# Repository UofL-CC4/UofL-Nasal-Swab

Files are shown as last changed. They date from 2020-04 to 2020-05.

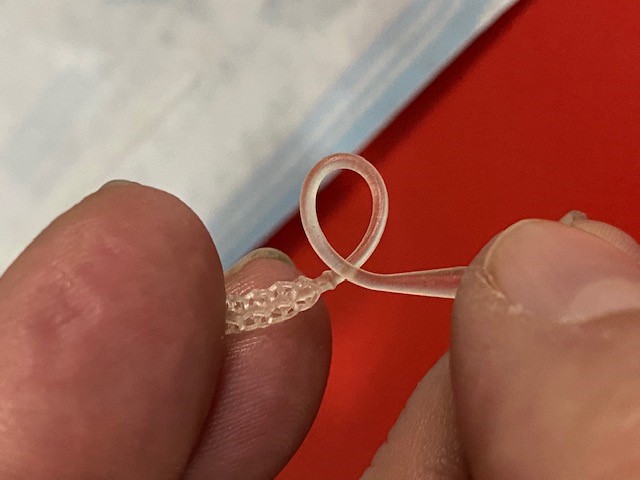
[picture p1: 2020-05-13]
Release R1 05_13_2020/Images/Swab Test.jpg

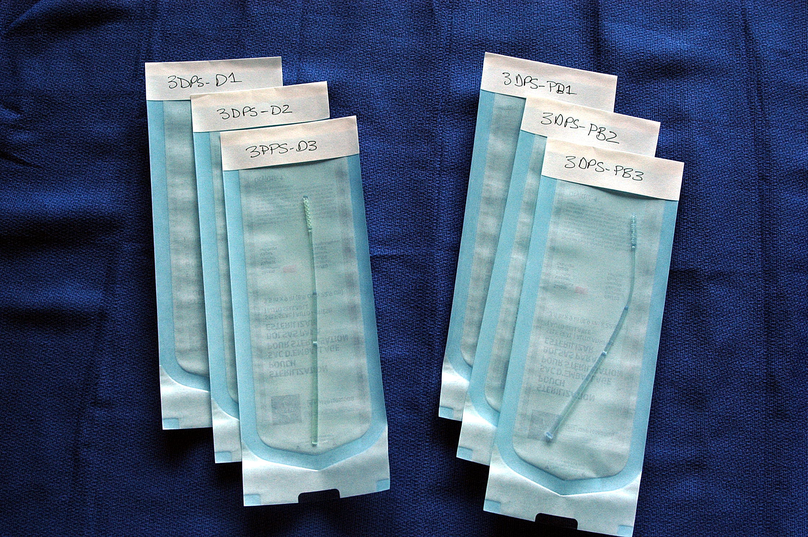
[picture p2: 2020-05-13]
Release R1 05_13_2020/Images/DSC_0561.JPG

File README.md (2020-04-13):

# UofL-Nasal-Swab
UofL Nasal Swab Data Package
We are running (side by side, (Standard Swab/3D Printed Swab)) testing with COVID19 patients to make sure we do not have a problem with false negatives, this is a mandatory clinical trial required by UofL Health Institutional Review Board (IRB).  Under FDA regulations, an IRB is an appropriately constituted group that has been formally designated to review and monitor biomedical research involving human subjects. In accordance with FDA regulations, an IRB has the authority to approve, require modifications in (to secure approval), or disapprove research. This group review serves an important role in the protection of the rights and welfare of human research subjects.

Here is where we are at;
•	We have developed the Creative Commons License for release of all data.
•	There is an online repository for all related files it is live but the final document package is not updated yet. https://github.com/UofL-CC4/UofL-Nasal-Swab
•	All clinical protocols are established and being followed in the IRB Clinical Trial
•	3D printing of the geometry has been clinically validated
•	COVID-19 3D Printed Swab Cleaning Protocol is complete
•	COVID-19 3D Printed Swab Curing Protocol is complete
•	COVID-19 3D Printed Swab Packaging Protocol is complete
•	ETO Sterilization protocol is complete
•	COVID 19 Test Kit Assembly Protocol is complete and SOP is complete
•	Viral transport Medium has been clinically validated using CDC recipe
We are now just waiting for IRB Sign off, we anticipate today.

We are currently building workflows for different 3D printers so we can roll this out Statewide with the current emphasis going to Lexmark and UK.

I have attached 2 videos one is of a completed SWAB print and the second is on the UV curing rack

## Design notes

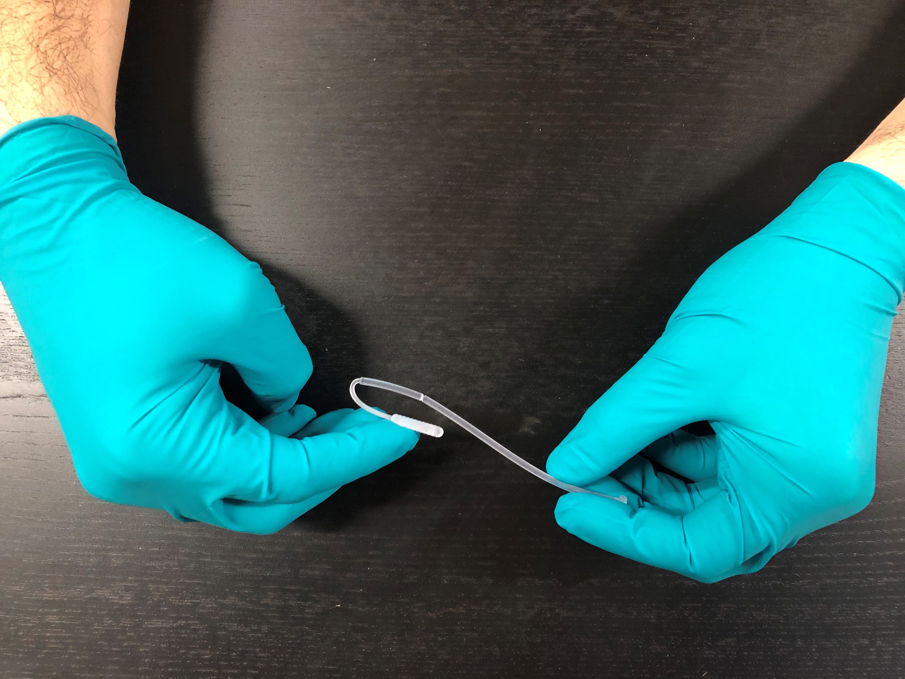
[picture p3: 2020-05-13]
Release R1 05_13_2020/Images/KS003.jpg

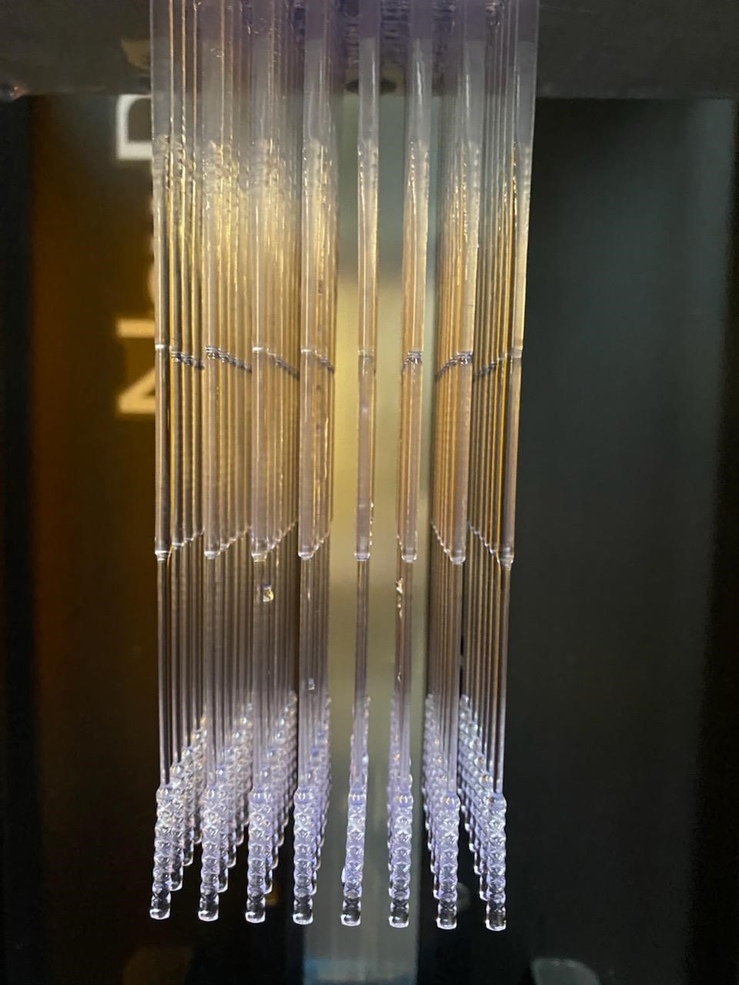
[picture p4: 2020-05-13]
Release R1 05_13_2020/Images/ET001.jpg

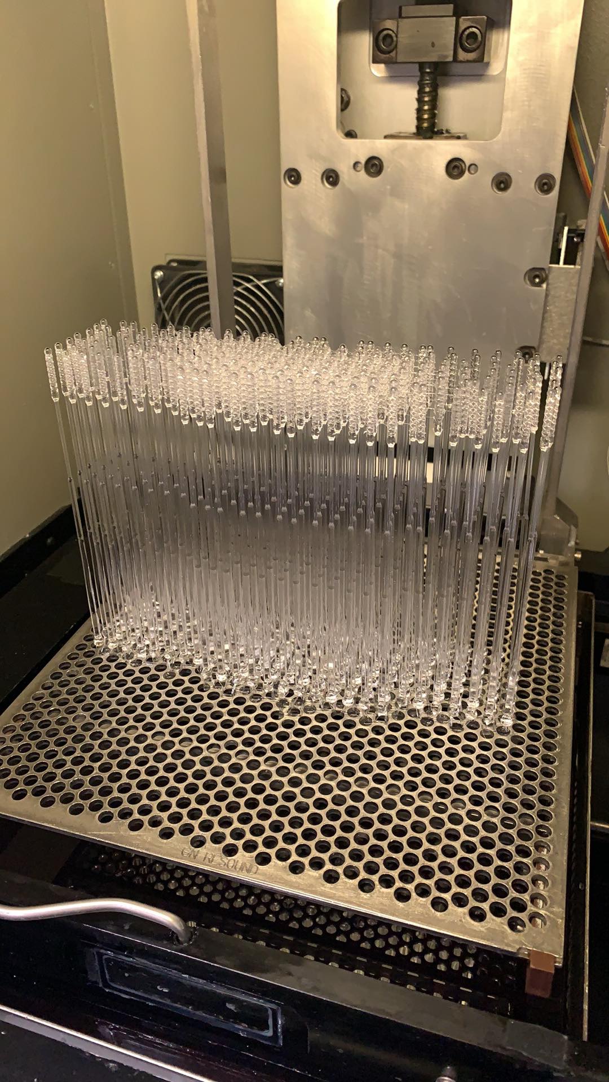
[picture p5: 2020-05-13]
Release R1 05_13_2020/Images/SLA_VIPER.jpg

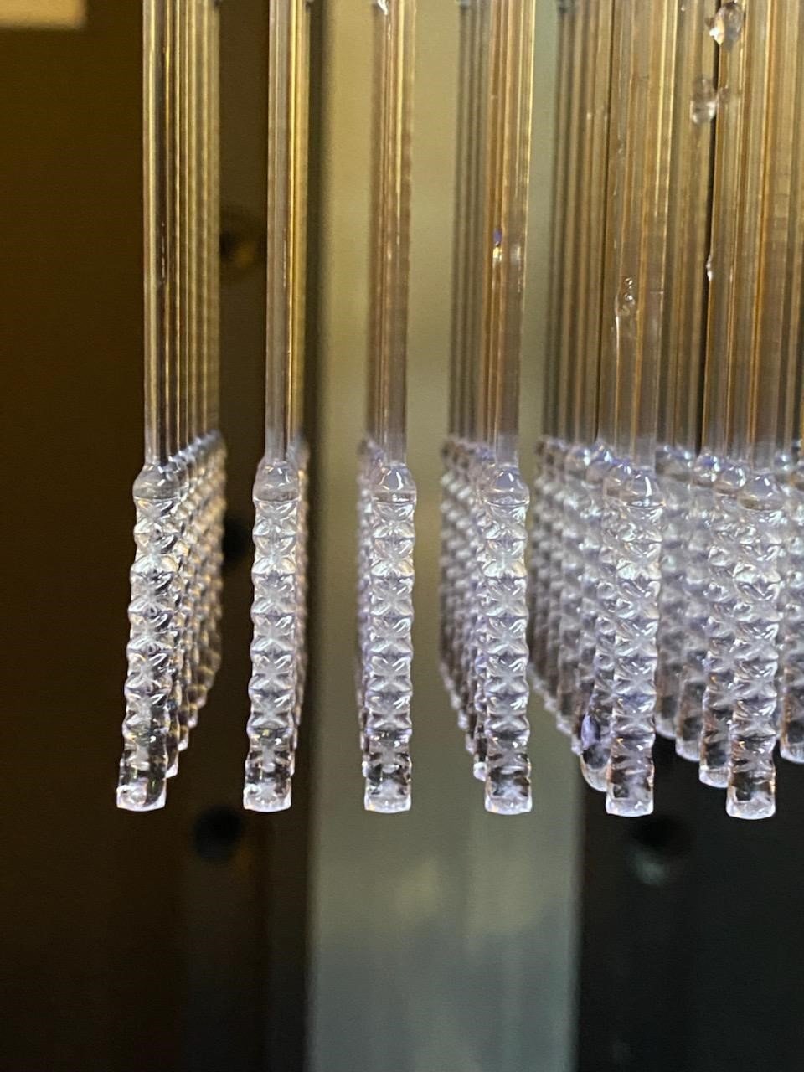
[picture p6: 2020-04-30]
Release R1 05_13_2020/Images/ET002.jpg

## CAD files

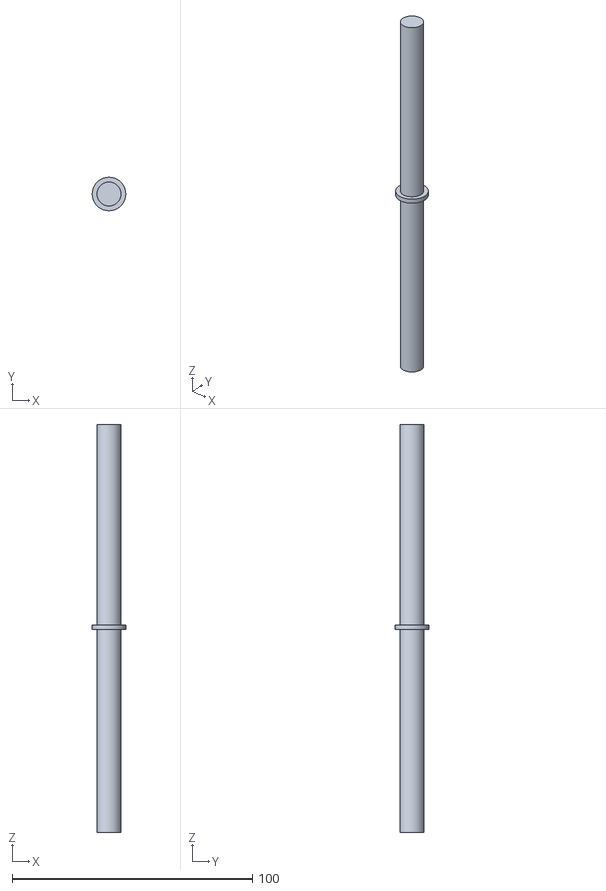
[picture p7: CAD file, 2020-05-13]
Release R1 05_13_2020/3D Printed Swab Curing Rack/Leg(x4).stl
14.0 x 14.0 x 170.0

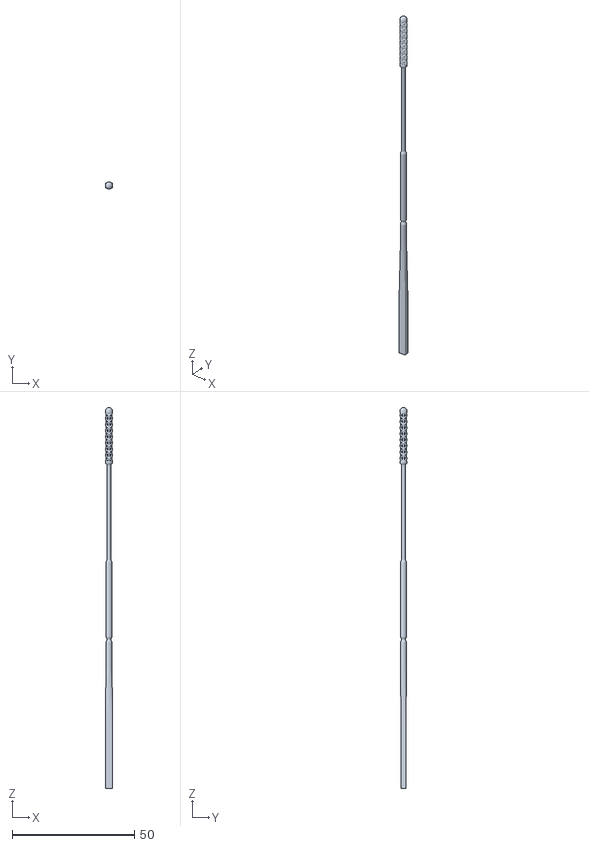
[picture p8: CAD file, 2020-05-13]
Release R1 05_13_2020/3D Swab Data File for Print/UofL Final swab 05012020.stl
3.00 x 3.00 x 156.0

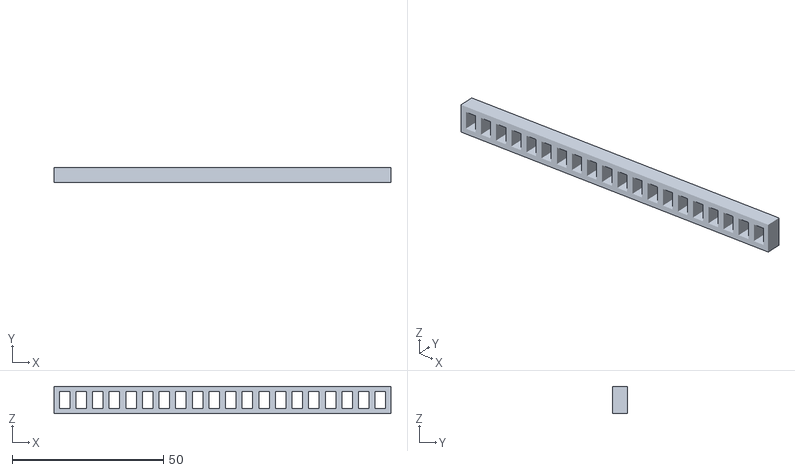
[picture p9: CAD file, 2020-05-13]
Release R1 05_13_2020/3D Printed Swab Curing Rack/End Cap.stl
111.5 x 5.00 x 9.00

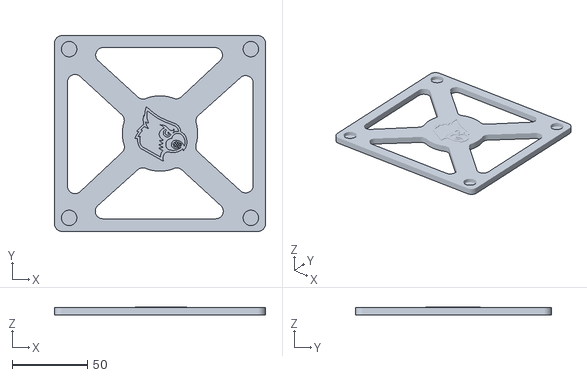
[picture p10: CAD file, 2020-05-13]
Release R1 05_13_2020/3D Printed Swab Curing Rack/Base.stl
140.0 x 130.0 x 5.50

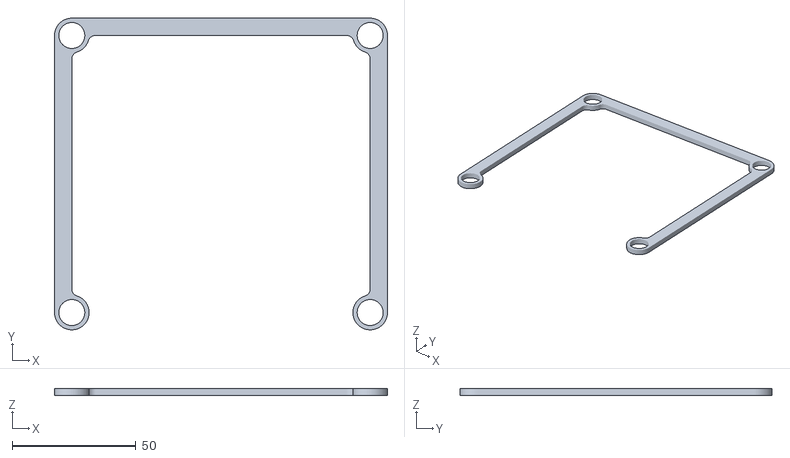
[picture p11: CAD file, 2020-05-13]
Release R1 05_13_2020/3D Printed Swab Curing Rack/Middle Support.stl
134.5 x 125.9 x 3.00

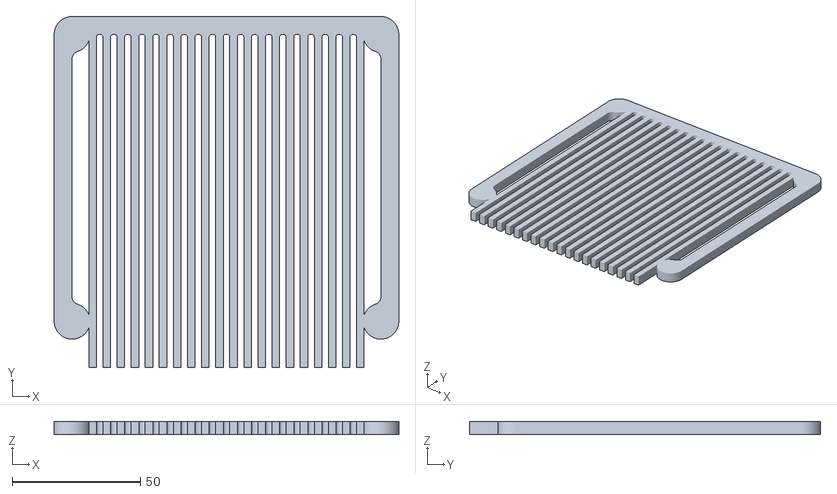
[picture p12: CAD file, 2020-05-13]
Release R1 05_13_2020/3D Printed Swab Curing Rack/Rack.stl
134.5 x 137.0 x 5.00

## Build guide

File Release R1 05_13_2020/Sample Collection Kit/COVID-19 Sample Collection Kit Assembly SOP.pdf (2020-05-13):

## Cardiovascular Innovation Institute

### Cardiovascular Dynamics and Surgical Technology Laboratory

Dr. George M. Pantalos
Rm. CII 423 & 424
Prepared by: George Pantalos [2 April 2020, Rev 1.1 8 April 2020]

Title: COVID-19 Sample Collection Kit Assembly

Document Type: Standard Operating Procedure

Purpose:
The objective of this procedure is to assemble COVID-19 culture sample collection kits.

Procedure:

Necessary Materials (to assemble 50 sampling kits; scale as needed):
Material Name | Quantity | Physical Description
Biohazard Level II Hood | 1 | Biosafety Cabinet, CII 424
Viral transport medium | > 150 mL | Red liquid
1000-5000 μL pipette Gilson P5000 | 1 | Navy and gray pipette
15mL Presterilized Falcon tube (vials) | 50 | Conical vial with screw cap
Sterile foam tipped sample swab | 50 | Puritan swabs packaged in paper
Biohazard bags | 50 | 6” x 9” Orange transparent bags
Instructions For Use labels | 50 | 3” x 6” printed label with adhesive back
Pipetman diamond tips | 5-10 | Reference No. VWR76178-180
Tube holder | 2-4 | Holds 50 15mL Falcon tubes
Pair of clean exam gloves | 2 | One pair for each technician
Hairnets | 2 | One for each technician
Disposable lab coat with cuffed sleeves | 2 | One for each technician
Surgical Mask | 2 | One for each technician
200 mL Sterile container | 1 | Open container to hold viral transport medium
Biohazard waste container | 1 | 12” x 12” x 24” container with red biohazard liner
Sample Collection Kit transport container | 1 | 4 gallon flip-top tote

1. Execution of Process 1: Preparation of Biohazard Sample Collection Bag (lab counter, Room 424)
Step Number | Action Taken | Depiction
1.1 | Gather all necessary materials.
1.2 | Cut Instructions For Use labels to size with paper cutter
1.3 | Adhere Instructions For Use label to the biohazard bag so the biohazard sign and storage indicators are visible.

### 2. Execution of Process 2: Filling Falcon Tubes with Viral Transport Medium (Biosafety

Cabinet, Room 424*)
Step Number | Action Taken | Depiction
2.1 | In the biosafety cabinet, while dressed in PPE, set up 50 falcon tubes in a tube holder and set an empty tube holder to the side.
2.2 | Prepare viral transport medium for pipetting and loosen caps of all Falcon tubes.
2.3 | Attach the sterile Pipetman tip to the pipet. If this tip ever touches anything other than the inside of the Falcon tubes or the viral medium, discard it in the biohazard waste container and replace it with aother sterile tip.
2.4 | Technician 1, draw up 3 mL viral transport fluid with the pipet.
2.5 | Technician 2, take off the lid of the first Falcon tube and hand container to Technician 1.
2.6 | Technician 1, dispense 3 mL into Falcon tube, and hand the container back to Technician 2.
2.7 | Technician 2, secure lid on the Falcon tube and place upside down on the hood countertop to check for leakage. Discard tube if leakage is observed.
2.8 | Repeat steps 2.4-2.7, until there are 50 filled Falcon tubes.
2.9 | Turn filled Falcon tubes right-side up and place into tube rack. Take rack of filled Falcon tubes to the Sampling Kit Assembly Area (hooded work bench), then dispose of pipette tip and gloves in the biohazard waste container

### 3. Execution of Process 3: Filling Sample Collection Bag with All Materials (Hooded Work

Bench, Room 423)
Step Number | Action Taken | Depiction
3.2 | Take a labeled biohazard bag and fill it with a packaged sterile foam swab and a filled Falcon tube, then securely close the biohazard bag. Place the closed bag in the Sample Collection Kit transport container.
3.3 | Repeat step 3.2 for 50 bags.
3.4 | Once all bags are filled and in the transport container, dispose of gloves, in the biohazard waste container. Due to the current PPE shortage, if coats, hairnets, and masks are in sufficient condition to be reused, they should be saved in a labeled container and reused at a later date by the same technician.

Maintaining Falcon Tube Sterility:
In addition to replacing contaminated tips, do not run hands or anything else over or near the open end of the tube when dispensing viral transport media. The inside cap must also say sterile. Only touch the outside of the cap. If the inside of the cap, or the inside of the tube becomes contaminated, the tube and any material inside must be discarded in the biohazard waste container. Maintaining sterility inside the tube is the most important priority.

Safety Hazards:
No sharps or virulent materials used. The PPE is for the protection and sterility of Falcon tube being used for the culture sample collection as well as protection for the technician from accidental solution splash.

Notes:
1) An additional biosafety cabinet (Class II hood) is available in the CII Room 512.
2) The kit assembly process (tube with media and sterile swab into labeled biohazard bag) does not need to take place in a hooded bench. If additional space is needed for production scale-up purposes, it can occur on a lab countertop covered with plastic-backed absorbent material.

Document Concurrence:

Clara Jones ________________ date _____________________

Sienna Shacklette _____________________ date _________________

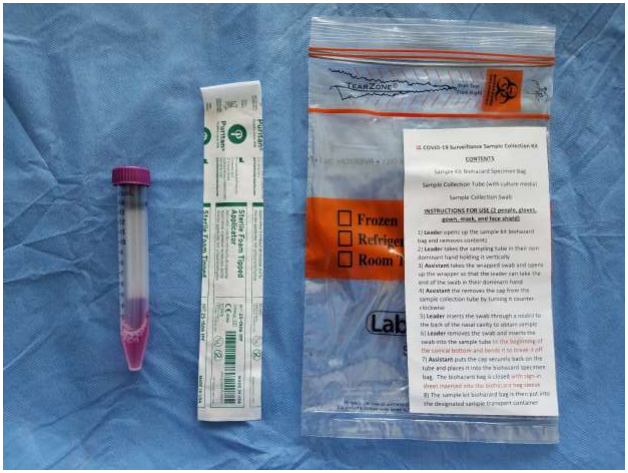
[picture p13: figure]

Example Sample Collection Kit including (left) the 15 mL Falcon Tube vial with 3 mL of viral transport media, (middle) sterile collection swab in sterile wrapper, and (right) the biohazard bag with Instructions For Use label attached to the right hand side of the front of the bag. A completed Sample Collection Kit has the 15 mL Falcon Tube and swab sealed inside of the biohazard bag for transport to the sampling site.

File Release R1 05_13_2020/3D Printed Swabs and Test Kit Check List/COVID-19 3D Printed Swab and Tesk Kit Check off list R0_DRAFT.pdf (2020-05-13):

## COVID-19 3D Printed Swabs and Test Kit CHECKLIST

# D R A F T

COVID-19 3D Print settings and resin protocol

AWAITING PROTOCAL DR. GRANT

COVID-19 3D Printed Swab Cleaning Protocol (Unsterile Clean Environment)

5 minute clean wash with <90% isopropyl alcohol (ultrasonic agitation preferred) 5 minutes wash with new clean alcohol <90% using (ultrasonic agitation preferred) Convection dry at 37C for 30 minutes

COVID-19 3D Printed Swab Curing Protocol (Unsterile Clean Environment)

Cure in UV curing box at 100% power capacity for 15 minutes
Max upper temp limit set to 60C

COVID-19 3D Printed Swab Packaging Protocol (Unsterile Clean Environment)

Using nitrile gloved hands package in sterilization pouch for sterilization procedure

ETO Sterilization protocol (Sterile, Clean Environment)

Preconditioning and humidification
Gas introduction
Exposure
Evacuation
Air washes

Viral Transport Media Protocol (utilizing CDC guidelines) (Sterile, Clean Environment)

From the WHO 2006 guidelines here is an alternative to commercial VTM:

A suitable VTM for use in collecting throat and nasal swabs from human patients is prepared as follows:

Add 10g veal infusion broth and 2g bovine albumin fraction V to sterile distilled water (to 400 ml).
Add 0.8 ml gentamicin sulfate solution (50 mg/ml) and 3.2 ml amphotericin B (250 μg/ml)
Sterilize by filtration.

COVID 19 Test Kit Assembly Protocol (Sterile, Clean Environment)

See attached SOP (COVID-19 Sample Collection Kit Assembly SOP.pdf)

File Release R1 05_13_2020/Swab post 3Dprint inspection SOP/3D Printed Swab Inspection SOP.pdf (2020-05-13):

## Cardiovascular Innovation Institute

### Cardiovascular Dynamics and Surgery Laboratory

Dr. George M. Pantalos
Rm. 423
Prepared by: Sienna Shacklette

Title: COVID-19 3D Printed Swab Inspection and Sterilization

Document Type: Standard Operating Procedure

Purpose:
The objective of this procedure is inspect the 3D printed swabs for imperfections and to prepare them for sterilization.

Procedure:
Necessary Materials:
Material Name | Quantity | Physical Description
3D printed swabs | Number upon delivery | Plastic swabs to be inspected
Small sterilization pouches | As needed | 1 per swab
Larger sterilization pouches | As needed | To place wrapped swabs inside
Sterilization indicator strip | As needed | 1 per larger sterilization pouch
Autoclave | 1
Pair of clean gloves | 1
Hairnet/surgical cap | 1
Disposable gown/jacket | 1
Mask | 1
Well-lit benchtop | 1
Dark drape or towel | 1 | Use as background
Magnifying glass/Headband Magnifier | 1

### 1. Execution of Process 1: Preparations for Inspection

Step Number | Action Taken | Depiction
1.1 | On the well-lit benchtop, lay down the dark drape/towel. This allows for contrast between the swabs and the background.
1.2 | Next, get the swabs and packages prepared for the next process. You will not want to have to stop to get supplies during inspection.

1.3 | Put on the gloves, hairnet/surgical cap, and the disposable gown/jacket.
1.4 | Next position your magnifying glass or headband magnifier so you can see with and without the magnifier.
1.5 | Assure all materials are collected before beginning the inspection and preparation process.

### 2. Execution of Process 2: Inspection of 3D Printed Swabs

Step Number | Action Taken | Depiction
2.1 | Approximately 10-20 swabs are laid out on the dark towel. This allows for a holistic inspection. Any obvious gross imperfections are removed from batch and placed into a reject pile.
2.2 | One at a time using the magnifier, each swab will be picked up and inspected. Inspection includes: • No imperfections on the stem of the swab that cannot be trimmed off by hand (See 1.3) • The tip is not broken • The tip is rendered correctly and has no imperfections that cannot be trimmed off by hand (See 1.3) • There is no debris on the swab • The swab is straight without significant curve or any deviations | Photographic examples show in Rejected Swabs Examples below.
2.3 | If there are any imperfections on the stem or tip, often they can be trimmed off by hand. If the imperfection is able to be removed, leaving the area smooth then this swab can be accepted.
2.4 | If there is a stump on the stem of the swab, use wire cutters to remove the stump from the swab. | Photographic examples show in Accepted Swabs Examples below.
2.5 | Swabs that are deemed acceptable for use will be placed in a separate pile from the rejects. | Photographic examples show in Accepted Swabs Examples below.
2.6 | Once each of the 10-20 swabs are inspected, repeat steps 2.1-2.4 until all swabs have been inspected. Remove

all reject swabs from the examination area.

### 3. Execution of Process 3: Preparing for Sterilization

Step Number | Action Taken | Depiction
3.1 | Once all acceptable swabs are inspected, start to place swabs in sterilization sleeves (peel packs). Pointing the bottom of the stem down and the tip up, place the swab all the way down in the packaging. You want it oriented so that when the package is peeled opened, the swab stem is available to remove the swab from the package.

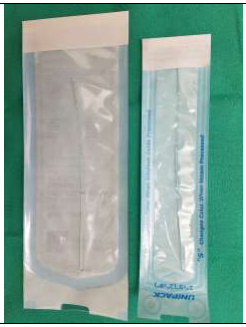
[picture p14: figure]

3.2

Once all swabs are placed in the sterile packaging, the adhesive cover can be removed and the small pouches can be closed.

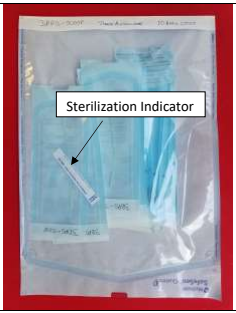
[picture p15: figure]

3.3 | Once all small pouches are sealed, place as many can comfortably fit inside the larger sterilization pouches, along with a sterilization indicator strip. | Sterilization Indicator
3.4 | Once all the larger pouched are full, seal the packages. These are now ready for the Autoclave.

### 4. Execution of Process 4: Sterilization & Kit Assembly

Step Number | Action Taken | Depiction
4.1 | Use the steam Autoclave on standard cycle parameters in the RFF in order to steam sterilize the swabs. (Note: these swabs can also be sterilized by an ETO gas sterilization process if available.)
4.2 | Once swabs are sterilized, the larger package can be opened and the smaller individual packages can be used to create sample collection kits.

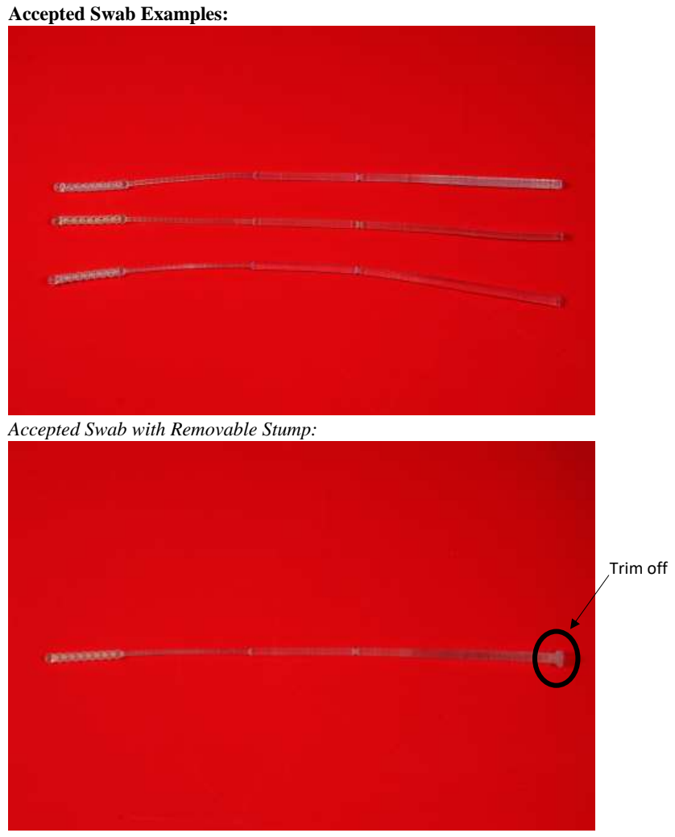
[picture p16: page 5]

Accepted Swab Examples:

Accepted Swab with Removable Stump:

Trim off

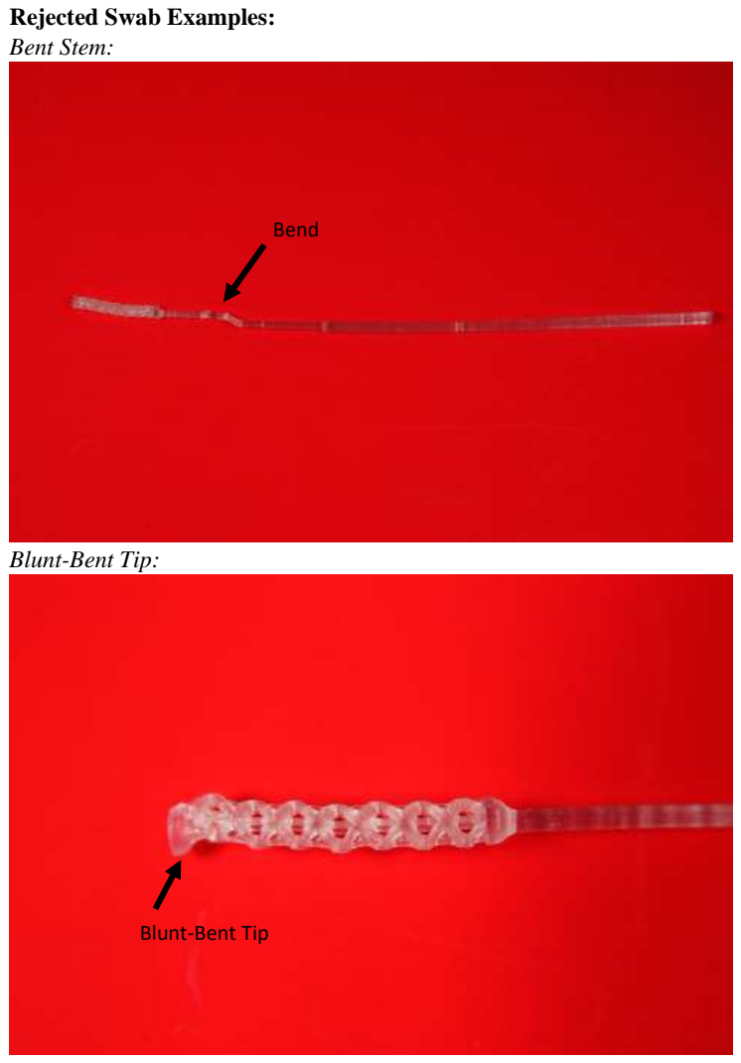
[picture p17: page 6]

Rejected Swab Examples:
Bent Stem:

Blunt-Bent Tip:

Bend

Blunt-Bent Tip

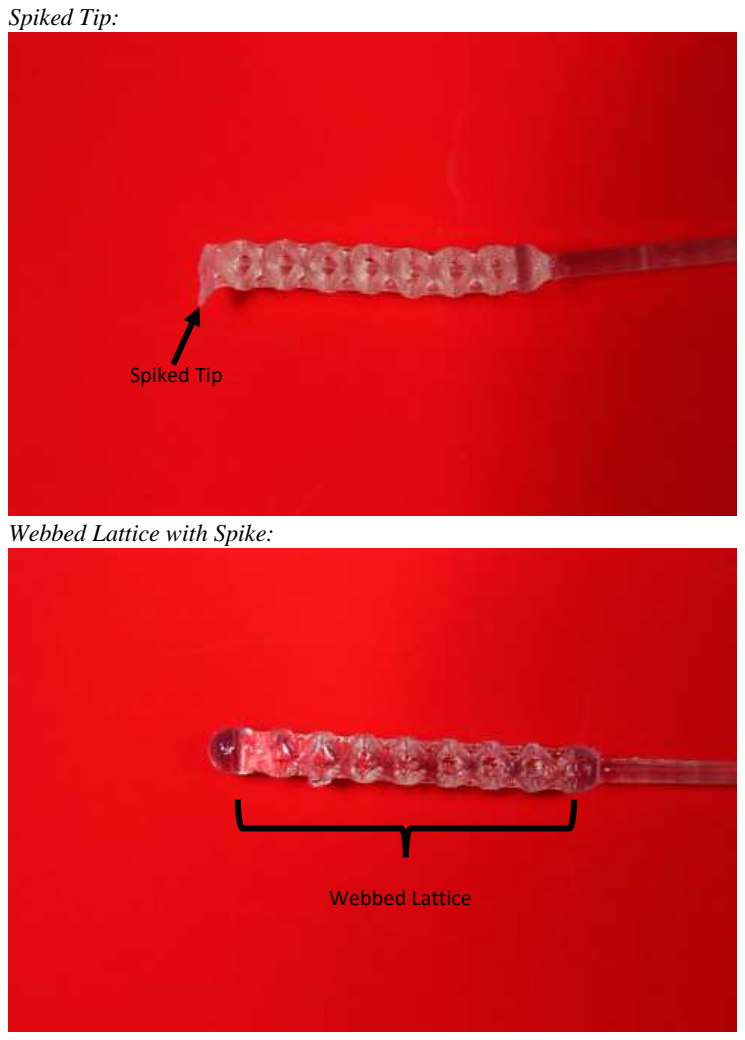
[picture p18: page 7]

Spiked Tip:

Webbed Lattice with Spike:

Spiked Tip

Webbed Lattice

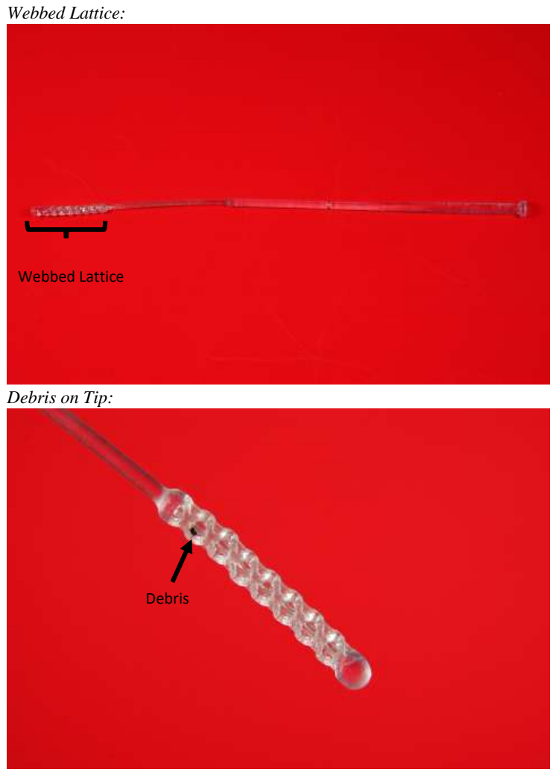
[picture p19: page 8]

Webbed Lattice:

Debris on Tip:

Webbed Lattice

Debris

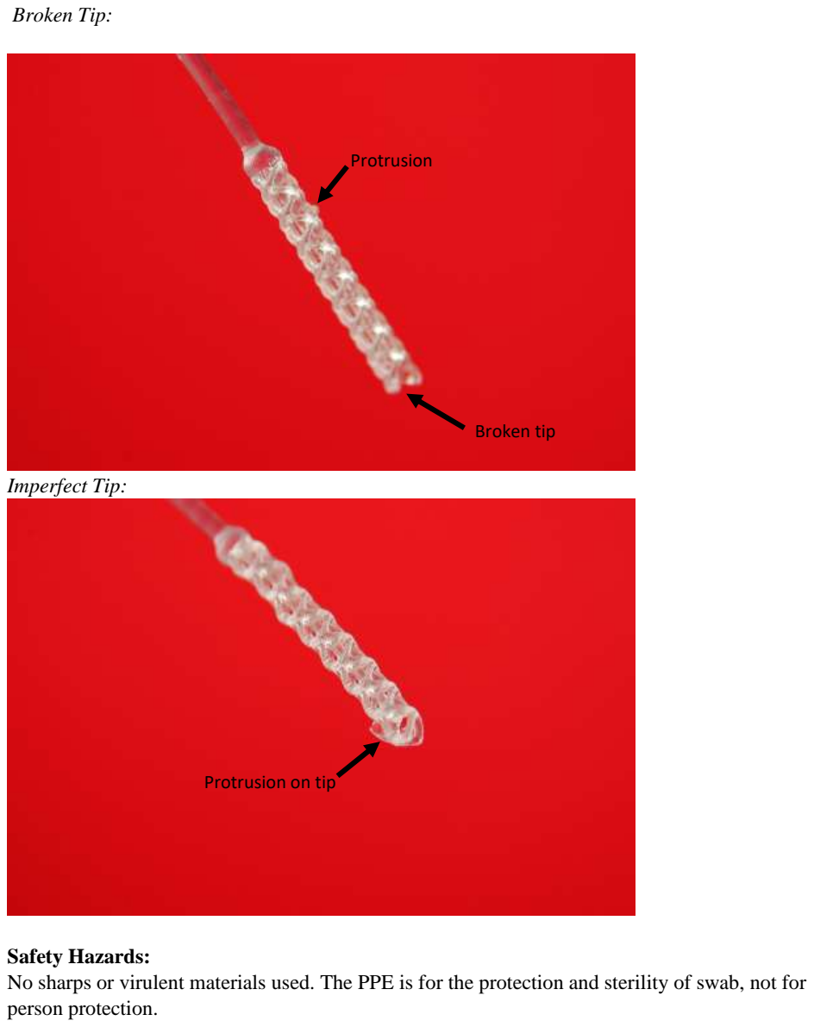
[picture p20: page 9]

Broken Tip:

Imperfect Tip:

Safety Hazards:
No sharps or virulent materials used. The PPE is for the protection and sterility of swab, not for person protection.

Protrusion

Protrusion on tip

Broken tip
